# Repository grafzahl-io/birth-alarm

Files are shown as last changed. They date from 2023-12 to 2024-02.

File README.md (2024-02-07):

# Birth alarm for horses

A simple and open source solution to get an alarm when your
horse foals.

The small device can be simply mounted on any horse holster.

Using a recharchable battery, WLAN and instant App notification for
Android and iOS.



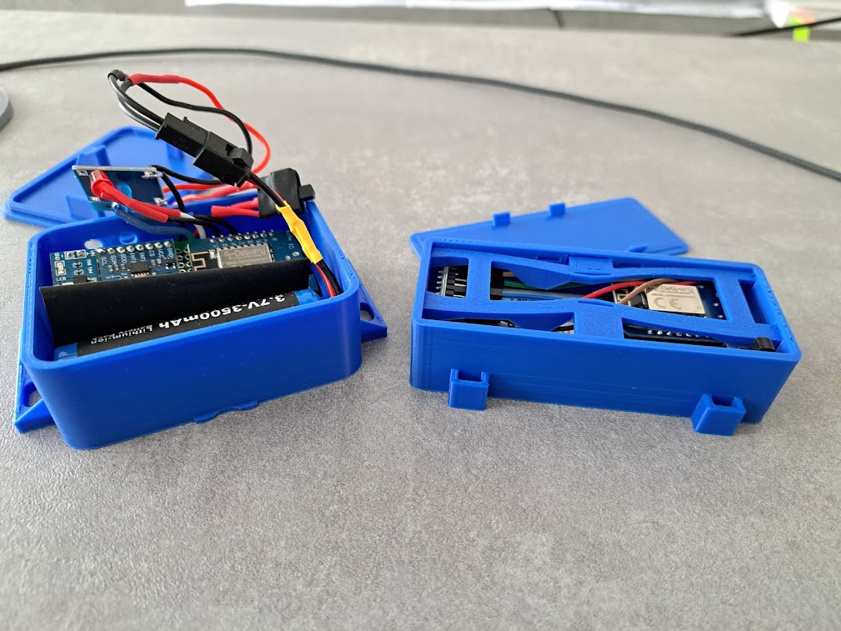
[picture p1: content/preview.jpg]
birth alarm device comparison between v1 and v2 Comparison between v1 and v2


## Tech Stack

**Device:** 3D printed case, rechargable battery, WLAN, customizable

**Server:** Go ([Gotify](https://gotify.net/) with Docker)

## FAQ

#### What is this good for?

This device is sending an instant alarm if the horse lies down to foal.

#### Why did you do this?

I looked for a proper device that is affordable without GSM as transmission method.
We have no cell phone network in our stable, but WLAN. I did not found any products
using WLAN with simple App notification - so I build it myself.

#### How does it work?

The device is mounted on the chin strap of the horse's holster. A gyro sensor is tracking the devices position and triggers an alarm if the horse lies down.
The push notification is sent to a server, where the registered Apps are notified.

## Roadmap v2

- improve sleep mode and add configuration for sensitivity
  
- improve case: simpler, more durable, waterproof
  
- reset button to reset wifi configuration and settings

## Roadmap v1

- creating a DIY manual for everyone to reproduce the device

- ~~configurable WLAN SSID and Password through Bluetooth~~

- ~~smaller battery and smaller device case~~

- ~~adding a measure unit to send an warning for low battery~~

- ~~replacing the hardware components with smaller ones~~

## Feedback

If you have any feedback, please reach out to us at info@grafzahl.io

## Authors

- [@grafzahl-io](https://github.com/grafzahl-io)

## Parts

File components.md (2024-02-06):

# hardware components (v2)
- arduino d1 mini (node mcu) (1x https://amzn.eu/d/cdpDF5X, 6,99€)
- accelerator sensor (Adafruit_ADXL345) (1x https://amzn.eu/d/e4jykyL, 6,99€)
- slide switch (1x https://amzn.eu/d/afPODNF, 7,98€)
- 4x 3,7V 2000mAh lithium battery 1S 1C LiPo (1x https://www.amazon.de/dp/B08TQSC5G9, 28,99€)
- battery shield for d1 mini (1x [https://www.az-delivery.de](https://www.az-delivery.de/products/batterie-shield-fuer-lithium-batterien-fuer-d1-mini?variant=20290872541280) 4,99 €)

# hardware components (v1)
- arduino d1 mini (node mcu) (1x https://amzn.eu/d/cdpDF5X, 6,99€)
- accelerator sensor (Adafruit_ADXL345) (1x https://amzn.eu/d/e4jykyL, 6,99€)
- blue 5mm led (1x https://amzn.eu/d/cWSqcIC, 8,99€)
- red 5mm led
- slide switch (1x https://amzn.eu/d/afPODNF, 7,98€)
- ams1117 3.3V power module (1x https://amzn.eu/d/j6Q5B1c, 3,99€)
- akku 18650 3.7V Li-ion 1200mah (1x https://amzn.eu/d/cP1gV2X, 15,99€)
- charger module (1x https://amzn.eu/d/bdrLuTi, 3,99 €)
- 330k resistor (1x https://amzn.eu/d/ahfti56, 12,00€)

# software components
- gotify instance (as a push notification server)

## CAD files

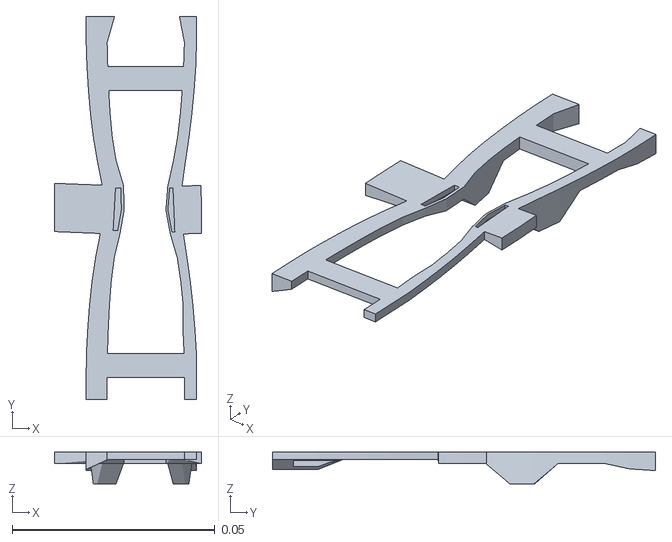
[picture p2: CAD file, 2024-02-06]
3d-print-case/v2/fixclamp-v2-13.stl
0.0363 x 0.0944 x 0.00787

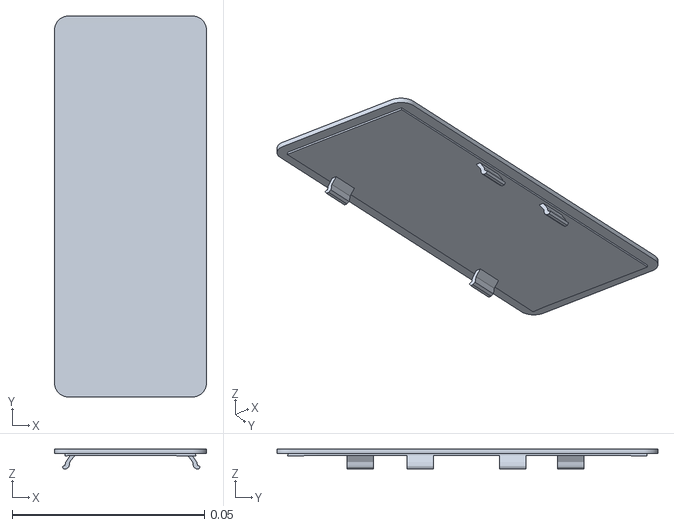
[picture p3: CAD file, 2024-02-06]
3d-print-case/v2/top-v2-13.stl
0.0395 x 0.099 x 0.00511

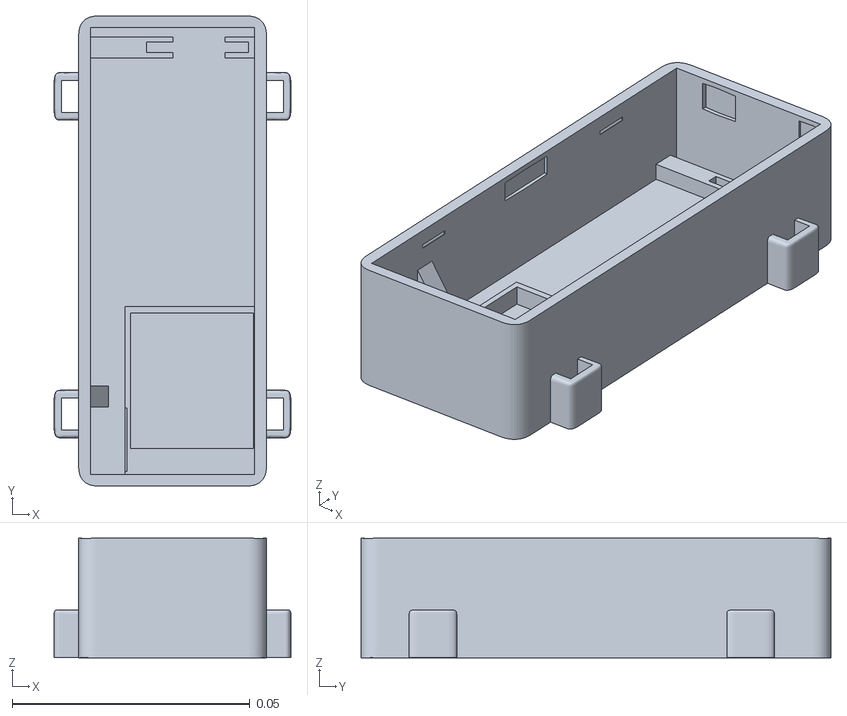
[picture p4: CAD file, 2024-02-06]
3d-print-case/v2/case-v2-13.stl
0.0498 x 0.0989 x 0.0252

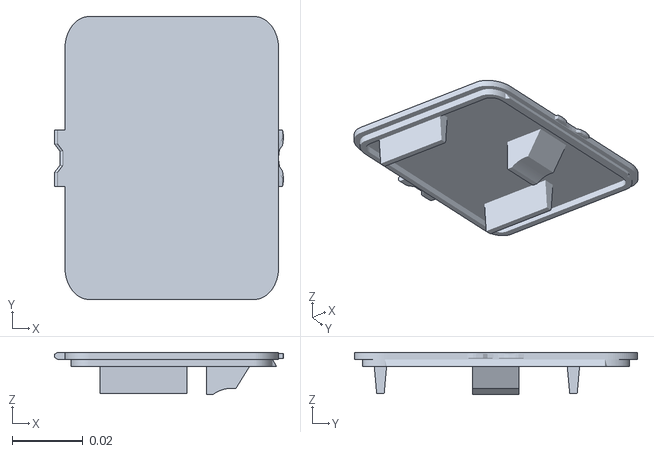
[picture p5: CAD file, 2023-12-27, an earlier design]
3d-print-case/v1/horse-birthalarm-b8-top.stl
0.0648 x 0.0801 x 0.012

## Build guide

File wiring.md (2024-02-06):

# wiring (v2)
- D5 => INT1 ADXL345
- D1 => SCL ADXL345
- D2 => SDA ADXL345
- 5V => VIN ADXL345
- GND => GND ADXL345

# wiring (v1)
- D7 => anode of red led
- D8 => anode of blue led
- D1 => SCL ADXL345
- D2 => SDA ADXL345
- 3V3 => VOUT of ams1117
- GND => V-OUT of ams 1117

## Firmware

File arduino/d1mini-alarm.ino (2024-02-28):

/*  ********************************************* 
 *  Birth alarm
 *  Utilizing Sparkfun's ADXL345 Library
 *  
 *  Development Environment Specifics:
 *  Arduino 2.2.1
 *  esp bordmanager version 2.4.2
 *  
 *  Hardware Specifications:
 *  SparkFun ADXL345 on ESP8266 D1 Mini
 * 
 * ADXL345 INT1 on PIN D5 / 15
 *         VNC on 5V
 *         SDA on D2
 *         SCL on D1
 *         GND on GND
 *  *********************************************/

#include <FS.h>
#include <ESP8266WiFi.h>
#include <DNSServer.h>
#include <ESP8266WebServer.h>
#include <WiFiManager.h>          // https://github.com/tzapu/WiFiManager
#include <ArduinoJson.h>          // https://github.com/bblanchon/ArduinoJson // install v5.0.8

#include <SparkFun_ADXL345.h>     // SparkFun ADXL345 Library
#include <ESP8266HTTPClient.h>

#include "user_interface.h"       // include required for LIGHT_SLEEP_T

/**
 * debug defnitions
 */
#define DEBUG 1
#if DEBUG == 1
  #define debug(x) Serial.print(x);
  #define debugln(x) Serial.println(x);
#else
  #define debug(x)
  #define debugln(x)
#endif

ADXL345 adxl = ADXL345();             // use adxl with i2c

int interruptPin = D5;                // Setup pin 2 to be the interrupt pin (d0 for most esp Boards)
int actInt = 0;
int inactive = 0;
int batteryPin = A0;
float lowVoltageThreshold = 3.73;     // est. 20% remaining battery cap.

String serverName = "https://push.birth-alarm.com/message";

// Set web server port number to 80
WiFiServer server(80);
//flag for saving data
bool shouldSaveConfig = false;
// Auxiliar variables to store the current output state
String outputState = "off";
// Assign output variables to GPIO pins
char output[2] = "5";
char pushToken[20];
char horseName[40];
// Variable to store the HTTP request
String header;

// milliseconds, to pause between push calls
unsigned long lastTime = 0;
unsigned long timerDelay = 2500;

int messageSent = 0;
int activeCylces = 0;
int sleepAfterXActiveCycles = 10;

void ADXL_ISR();

/**
 * builds wifi connection
 */
void connectToWifi() {
  debugln("Connecting");
  while(WiFi.status() != WL_CONNECTED) {
    delay(500);
    debug(".");
  }
  debugln("");
  debug("Connected to WiFi network with IP Address: ");
  debugln(WiFi.localIP());
}

/**
 * to be calledin loop
 */
void sendAlarm(String alarmType) {
  if ((millis() - lastTime) > timerDelay) {
    //Check WiFi connection status
    if(WiFi.status()== WL_CONNECTED){
      WiFiClientSecure client;
      HTTPClient http;

      client.setInsecure();

      String serverPath = serverName + "?token=" + pushToken + "&";
      
      // Your Domain name with URL path or IP address with path
      http.begin(client, serverPath);
      // Specify content-type header
      http.addHeader("Content-Type", "application/x-www-form-urlencoded", false, true);
      // Data to send with HTTP POST
      String httpRequestData = "Error";
      debugln(alarmType);
      if(alarmType == "birthalarm") {
        String horseNameS = "";
        horseNameS.concat(horseName);
        String titleMessageParams = "title=Geburt-Alarm!&message=";
        httpRequestData = titleMessageParams + horseNameS + " hat sich hin gelegt!&priority=10&";
      }
      if(alarmType == "lowbattery") {
        String horseNameS = "";
        horseNameS.concat(horseName);
        String titleMessageParams = "title=Niedriger Akkustand!&message=";
        httpRequestData = titleMessageParams + "Bitte lade den Akku für " + horseNameS + " Geburtenmelder&priority=10&";
      }
      // Send HTTP POST request
      debug(serverPath);
      debug(httpRequestData);
      int httpResponseCode = http.POST(httpRequestData);
      if (httpResponseCode > 0) {
        debug("HTTP Response code: ");
        debugln(httpResponseCode);
        String payload = http.getString();
        debugln(payload);
      }
      else {
        debug("Error code: ");
        debugln(httpResponseCode);
      }
      // Free resources
      http.end();
      messageSent = 1;
      // clear active cylcles
      activeCylces = 0;
    } else {
      debugln("WiFi Disconnected - reconnect");
      WiFi.forceSleepWake();
      WiFi.begin();
      connectToWifi();
    }
  }
}

void setupGyroSensor() {
  adxl.powerOn();                     // Power on the ADXL345

  adxl.setLowPower(true);             // set low power consumption
  adxl.setRangeSetting(4);            // Give the range settings
                                      // Accepted values are 2g, 4g, 8g or 16g
                                      // Higher Values = Wider Measurement Range
                                      // Lower Values = Greater Sensitivity

  adxl.setSpiBit(0);                  // Configure the device to be in 4 wire SPI mode when set to '0' or 3 wire SPI mode when set to 1
                                      // Default: Set to 1
                                      // SPI pins on the ATMega328: 11, 12 and 13 as reference in SPI Library 
   
  adxl.setActivityXYZ(1, 0, 0);       // Set to activate movement detection in the axes "adxl.setActivityXYZ(X, Y, Z);" (1 == ON, 0 == OFF)
  adxl.setActivityThreshold(145);      // 62.5mg per increment   // Set activity   // Inactivity thresholds (0-255)
 
  adxl.setInactivityXYZ(1, 0, 0);     // Set to detect inactivity in all the axes "adxl.setInactivityXYZ(X, Y, Z);" (1 == ON, 0 == OFF)
  adxl.setInactivityThreshold(20);    // 62.5mg per increment   // Set inactivity // Inactivity thresholds (0-255)
  adxl.setTimeInactivity(10);         // How many seconds of no activity is inactive?

  adxl.setTapDetectionOnXYZ(0, 0, 0); // Detect taps in the directions turned ON "adxl.setTapDetectionOnX(X, Y, Z);" (1 == ON, 0 == OFF)
 
  // Set values for what is considered a TAP and what is a DOUBLE TAP (0-255)
  adxl.setTapThreshold(50);           // 62.5 mg per increment
  adxl.setTapDuration(15);            // 625 μs per increment
  adxl.setDoubleTapLatency(80);       // 1.25 ms per increment
  adxl.setDoubleTapWindow(200);       // 1.25 ms per increment
 
  // Set values for what is considered FREE FALL (0-255)
  adxl.setFreeFallThreshold(2);       // (5 - 9) recommended - 62.5mg per increment
  adxl.setFreeFallDuration(10);       // (20 - 70) recommended - 5ms per increment
 
  // Setting all interupts to take place on INT1 pin
  adxl.setImportantInterruptMapping(1, 1, 1, 1, 1);     // Sets "adxl.setEveryInterruptMapping(single tap, double tap, free fall, activity, inactivity);" 
                                                        // Accepts only 1 or 2 values for pins INT1 and INT2. This chooses the pin on the ADXL345 to use for Interrupts.
                                                        // This library may have a problem using INT2 pin. Default to INT1 pin.
  
  // Turn on Interrupts for each mode (1 == ON, 0 == OFF)
  adxl.InactivityINT(1);
  adxl.ActivityINT(1);
  adxl.FreeFallINT(0);
  adxl.doubleTapINT(0);
  adxl.singleTapINT(0);
  
  attachInterrupt(digitalPinToInterrupt(interruptPin), ADXL_ISR, RISING);
}

void setup(){
  Serial.begin(9600);
  delay(1000);
  debugln("------------");
  debugln("BIRTH ALARM");
  debugln("------------");

  setupWifiManager();
  delay(2500);
  setupGyroSensor();
}

/****************** MAIN CODE ******************/
/*     Accelerometer Readings and Interrupt    */
void loop() {
  if(inactive == 1) {
    debugln("sleep now...");
    inactive = 3; // sleep mode
    lightSleep();
  }

  if(inactive == 0) {
    delay(2500);
    // restet inactive state
    // or go to sleep if we reached max active cycles
    if(messageSent == 1 || activeCylces > sleepAfterXActiveCycles) {
      debugln("*** INACTIVITY ***");
      //add code here to do when inactivity is sensed
      inactive = 1;
      lastTime = millis();
      messageSent = 0;
      activeCylces = 0;
    }

    debugln("*** ACTIVITY ***"); 
    // Accelerometer Readings
    int x,y,z;   
    adxl.readAccel(&x, &y, &z);         // Read the accelerometer values and store them in variables declared above x,y,z
    debugln(x)

    // send alarm
    if(x > 94 || x < -94) {
      // send alarm
      sendAlarm("birthalarm");
    } else {
      // increment active cylces to prevent hanging active when not reaching thresholds
      activeCylces = activeCylces + 1;
    }
    //add code here to do when activity is sensed
    checkBattery();
  }
}

void lightSleep(){
  WiFi.mode(WIFI_OFF);
  delay(100);
  wifi_fpm_set_sleep_type(LIGHT_SLEEP_T);
  wifi_fpm_open();
  gpio_pin_wakeup_enable(interruptPin, GPIO_PIN_INTR_HILEVEL);
  wifi_fpm_do_sleep(0xFFFFFFF);
}

void ICACHE_RAM_ATTR ADXL_ISR() {
  byte interrupts = adxl.getInterruptSource();
  if(adxl.triggered(interrupts, ADXL345_ACTIVITY)) {
    debugln("wake! activity")
    inactive = 0;
  }
  if(adxl.triggered(interrupts, ADXL345_FREE_FALL)) {
    debugln("wake! free fall")
    inactive = 0;
  }
}

//callback notifying us of the need to save config for wifi
void saveConfigCallback () {
  debugln("Should save config");
  shouldSaveConfig = true;
}

void checkBattery() {
  int rawValue = analogRead(batteryPin);
  float voltage = 4.2 * (rawValue/ 1023.0);  // calculate voltage: ref v / 10bit 
  debugln("Current battery voltage: " + String(voltage) + "V");

  if (voltage < lowVoltageThreshold) {
    debugln("send warning for low voltage!");
    sendAlarm("lowbattery");
  }
}
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

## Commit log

2024-02-06 Added working light sleep with pin interrupt + wifi config
    It contains a configuration step (still just at the very beginning, need to add a button to reset it and reconfigure WLAN)
    uses light sleep for longer battery life and sends a message for birth alarm and low battery to the notification server
2024-02-06 Update wiring.md
    Add v2 setup for wiring
2024-02-06 Add v2 of the 3d printed case
    [case-v2-13.stl, fixclamp-v2-13.stl, horse-birthalarm-b8-top.stl, top-v2-13.stl]
2024-02-28 Change sensibilty after tests and remove freefall as well as setting power save mode

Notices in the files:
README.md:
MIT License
